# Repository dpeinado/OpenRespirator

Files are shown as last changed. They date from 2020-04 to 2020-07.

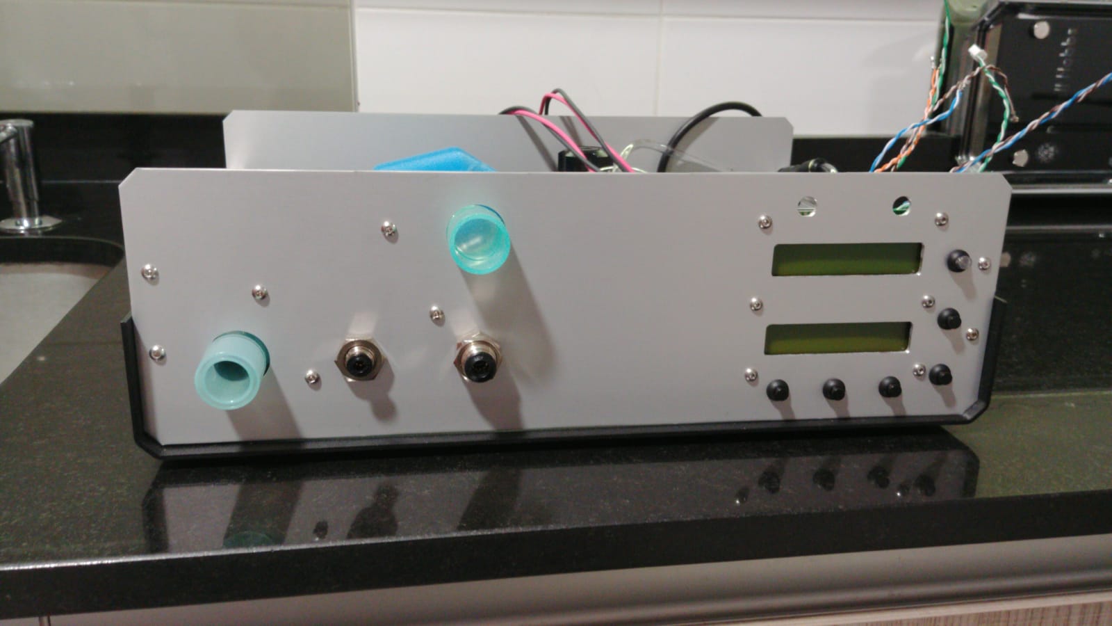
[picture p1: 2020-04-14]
Doc/Images/First assembly_4.jpeg

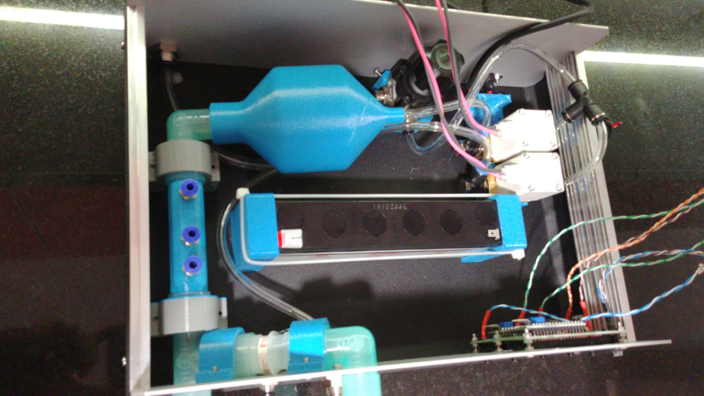
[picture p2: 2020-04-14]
Doc/Images/First assembly_5.jpeg

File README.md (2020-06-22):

# OpenRespirator
Software & Hardware for Open Respirator Project <br>

HW and system dodumentation are in the Doc directory <br>

## Contributors
- The system design is done by: Frede Jensen <br>
- Project coordination: Enrique Ramirez and Ramon Ruiz (Ennomotive) <br>
- Hardware & Software: David Ortiz, Rubén Perez de Aranda and Carlos Pardo <br>
- Collaborators: 
- - Intersurgical: Sara Rodriguez, Bill Barners, Mike Hinton <br>
- - Vithas Sanidad : Ignacio Narvaez <br>
- - McFly: Enrique, Marino y Daniel
  
## Sponsors: <br>

## ToDo list
### System

### Assembly

### Production
- Prepare production documentation
- - Define part alternatives
- Define production test & calibration
### Electronics
- Documentation
- - Electronics production test
### Firmware
- Monitor:
- Controller:
### Test & Validation
- Clinic test:
### Certification
- Documentation
- Presented to gobernment

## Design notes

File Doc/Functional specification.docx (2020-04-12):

# Emergency Ventilator

# Functional specification

Issue/change record

Issue | Date | Author | Reason of issue/summary
0.A | 10/04/2020 | | DRAFT, released for ongoing development

# Introduction

This document contains the full concept hardware and software design. The design is intended for the 75% of intensive care beds that are yet to be established in makeshift facilities.

# 1 Pressure Controlled SIMV

For purpose of simplicity, the ventilator operates in conventional Pressure Controlled SIMV (Synchronised Intermittent Mandatory Ventilation) mode of ventilation only. The ventilator will secure a set number of breaths per minute, by firstly attempting to synchronize the mechanical delivery of breaths with patient’s spontaneous efforts. If the patient fails to spontaneously take a needed breath, then the ventilator delivers it mandatorily.

To prevent a ‘fight’ between the patient and the ventilator, the ventilator reschedules the mandatory breath that follows a successfully synchronized spontaneous breath by 1 second.

SIMV behaves as PSV (Pressure Support Ventilation) when the patient makes full efforts, and it behaves as CMV (Continuous Mandatory Ventilation) if the patient does not make any efforts. When used with a mask on a conscious, spontaneously breathing patient, the SIMV behaves as nPSV or Synchronised BiPAP (by setting IP low). Switching the IP cycle off (or setting it equal to PEEP) makes SIMV behaves as CPAP (whether the patient is intubated or has a mask interface).

# 2 Functional specification

This section describes how the required performance characteristics (see General Description) are met.

### 2.1.1 User interface

The user interface is very simplified (and somewhat industrial looking). The top half of the facia is the monitoring interface. The bottom half is the controlling interface.

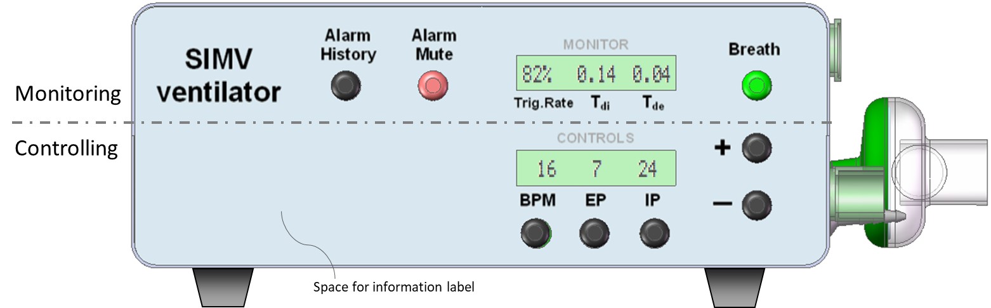
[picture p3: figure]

The process for adjusting a control paraments:

1. Press parameter control button.
2. Observe that the parameters value starts flashing (will time out after 5 sec inactivity).
3. Adjust the flashing parameter value using the +/- buttons.
4. Press parameter control button again to confirm the new setting.

The ‘Breath’ button has an integral green light. This flashes for 0.5s every time a spontaneous breath is detected. This provides an at a glance status of the patient, which can be seen at a distance across a room.

Pressing the green ‘Breath’ button delivers a manual breath. This is used to re-recruit the lung following a procedure that temporarily disconnected the patient from the ventilator, such as during suctioning or while changing the FiO2 level.

The ‘Alarm Mute’ button has an integral red light, which flashes under an alarm condition. Pressing the button will cancel the alarm event and suspend further alarms for 120 seconds.

The ‘Alarm History’ cycles through the last 10 alarm messages.

Alarm messages appear in the monitor (top) LCD display, where they overwrite the monitored parameters from 2.5 seconds every 3 seconds – i.e. the monitored values flash up for 0.5 seconds every 3 seconds while an alarm message is displayed.

The alarm message ‘Monitor Fail’ is detected by the controller and is displayed in the lower LCD.

Hospital staff commonly write information or place labels on their medical equipment, such as giving the device an identifiable name or number, or placing a reminder label. The facia is given a space for this. Below is an example reminder label that may be useful for certain personnel – without crowding the facia and detract from its simplicity.

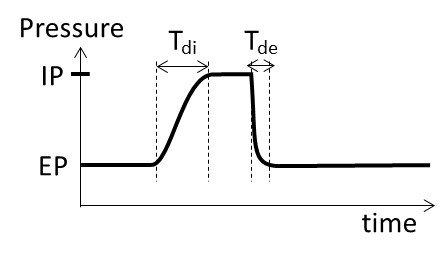
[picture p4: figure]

To power up the ventilator, press the ‘ON/OFF’ switch on the rear. Observe the power-up self-test correctly displays LEDs and the display digits.

To power down the ventilator, press the ‘ON/OFF’ switch on the rear. The monitor will display a message for 5 seconds saying ‘Power OFF?’. During this short period, press and hold any of the facia buttons for 2 seconds. If the 5-second message is missed, then simply flick the ‘ON/OFF’ switch again, to restart the 5-second message.

If none of the buttons are held for 2 seconds, or just pressed momentarily, the message will disappear and the ventilator will continue to operate under battery power. This enables moving the patient or intra-hospital transport.

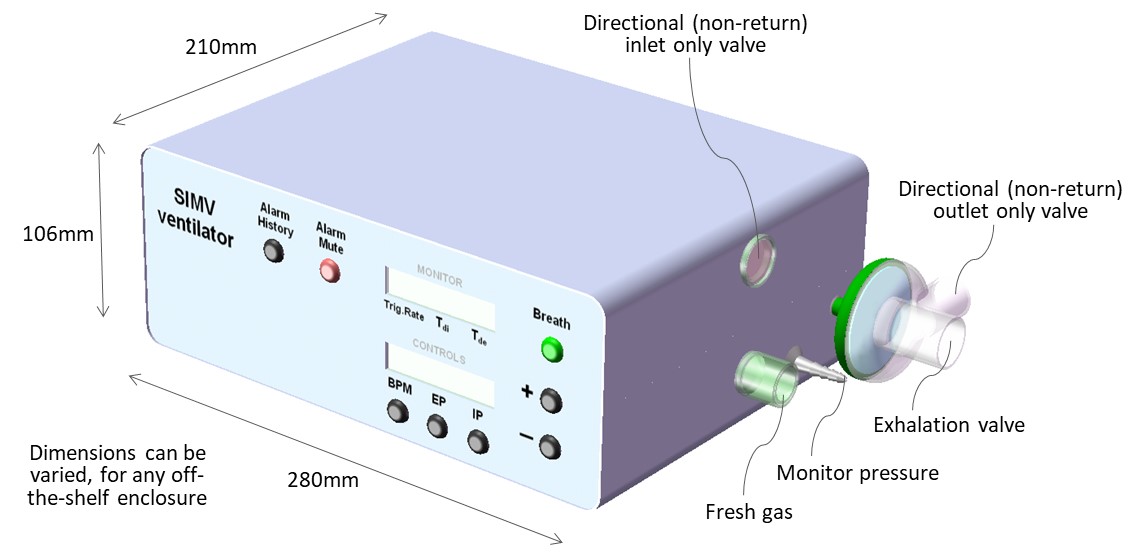
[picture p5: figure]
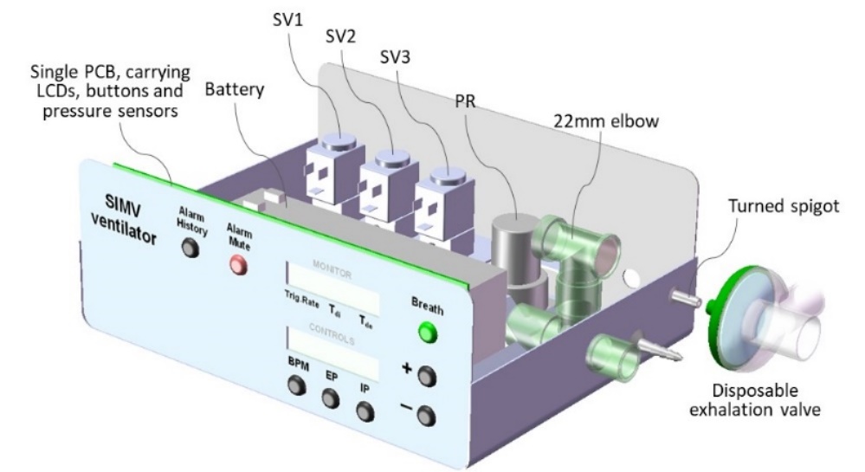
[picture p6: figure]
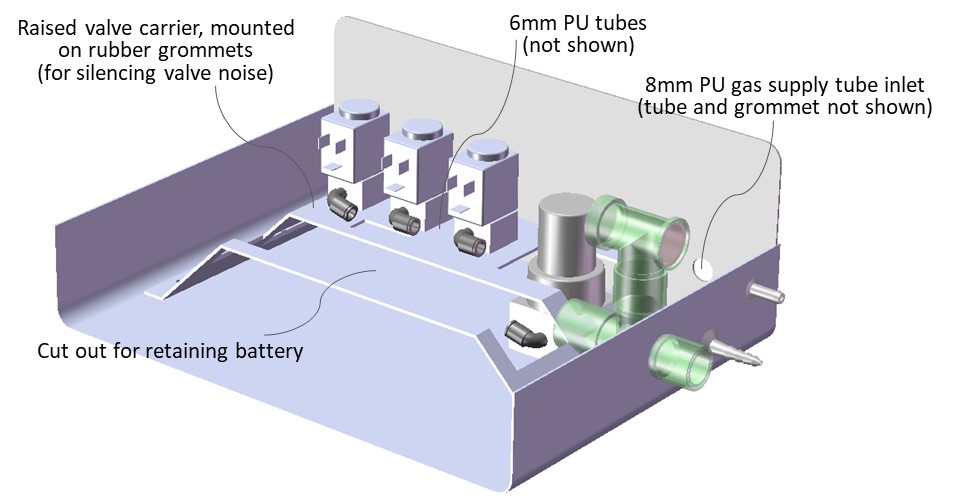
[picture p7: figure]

### 2.1.2 Schematic diagram

The Monitor and Controller operate independently, in parallel, observing each other (watchdogs). This assures the detection and alarming on any single failure mode. Both the controller and the monitor are capable of detecting an excess pressure (>40 mbar) and each can shut down the supply gas. This duality safeguards that compressed gas does not reach the patient circuit. All valves are NC (normally closed) types and will default to shutting off gas supply in case of total (battery) power failure.

The Controller operates its own user interface, for adjusting the parameters (BPM, EP and IP). The Controller reports its 3 parameters values every 50mS across an I2C serial interface with the Monitor. The Controller also reports when a valid change is made via the user interface. If the Monitor does not acknowledge receipt, then the Controller will instigate an alarm.

If the Controller reported ventilator paraments changes, without a prior valid user change, then it would indicate the Controller memory has corrupted. The Monitor will then alarm and can shut down gas supply if hazardous conditions occur.

The Monitor also calculates the triggered breath rate (patient effort) and the wave rise/decay times (Tdi and Tde, which indicates lung/system status). It will alarm if these deviate from tolerances.

On shut-down, the patient can breathe ambient air through the 2 directional NR valves.

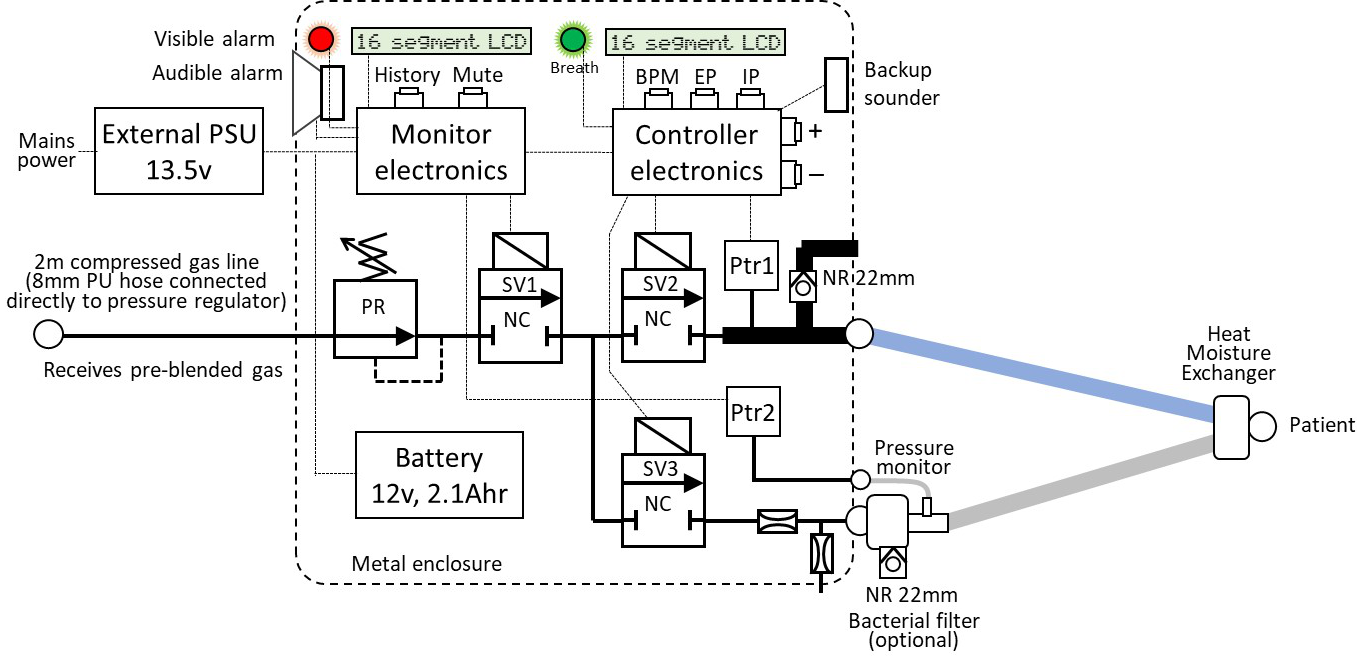
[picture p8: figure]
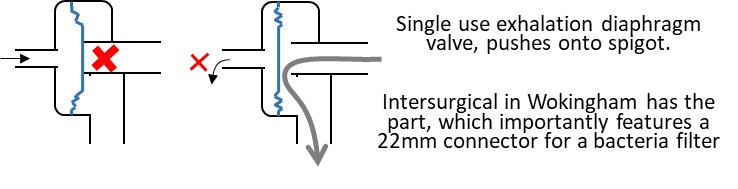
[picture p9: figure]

### 2.1.3 Ventilator operation flow chart

The Controller cycles the pressure wave in accordance with the set parameters (BPM, EP and IP). The inspiration cycle is instigated on breath detection, or if the mandatory cycle time is reached.

‘Open SV3’ has the effect of closing the exhalation valve – i.e. it should be read as ‘close exhalation valve’.

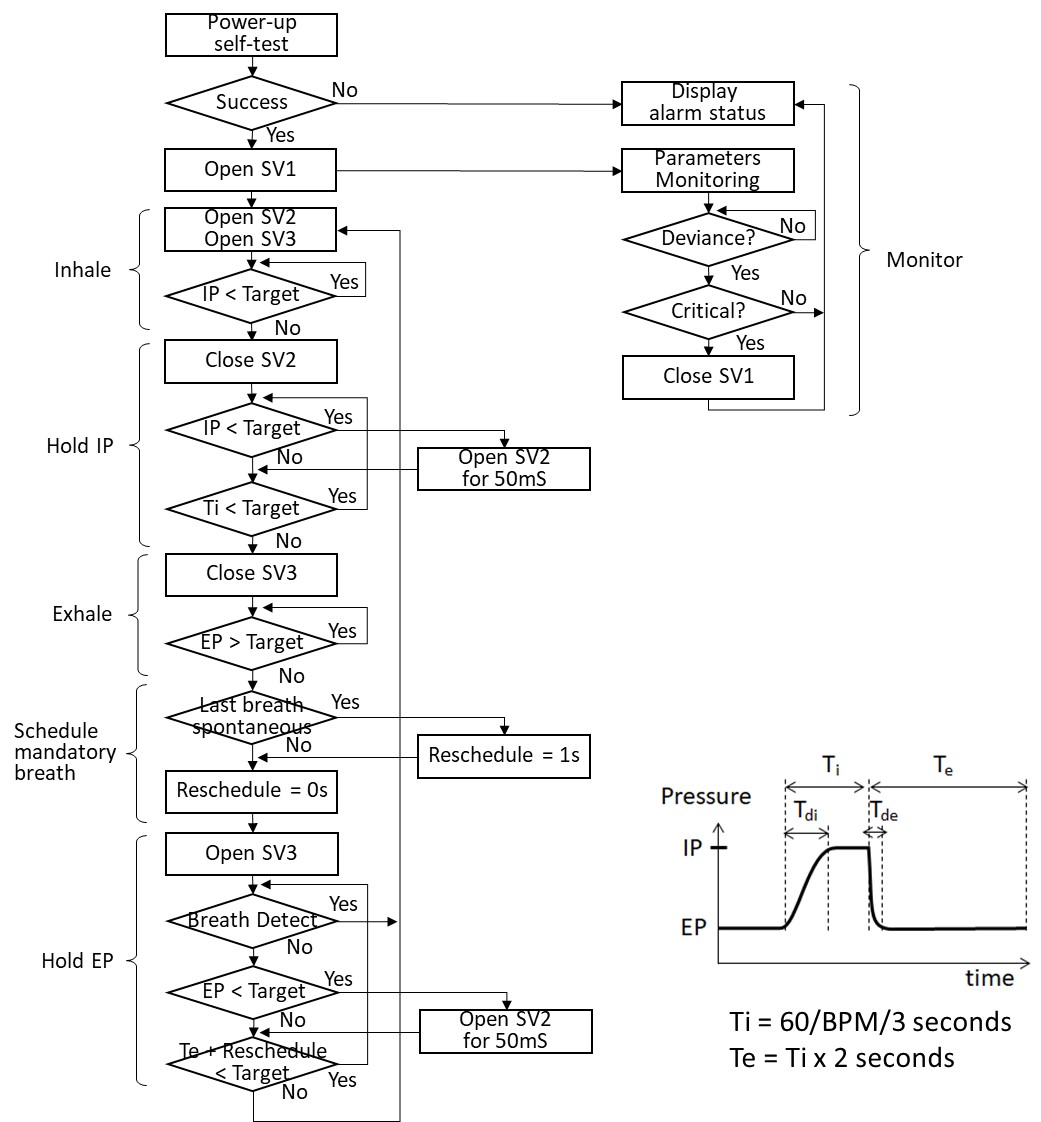
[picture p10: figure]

The steps ‘IP < Target’ and ‘EP > Target’ are likely to result is a small overshoot if implemented in their simplest form, due to the solenoid valve inertia/response time. The step will likely have some sub-steps to compensate for this, for example:

a) One approach: Once the ventilator user sets a new Target the initial breath cycle will use ‘IP < Target x 95%’. If this first breath undershoots, then the next cycle can be increased to ‘IP < Target x 96%). Keep incrementing until the intended IP is met and then freeze this setting. Do the same in reverse for reaching EP. The first cycle might use ‘EP > Target x 105%’ and then decrement this correction factor. Freeze the correction factor once the intended EP is reached. It could take 2 or 3 breaths for the ventilator to settle the IP and EP after a setting is changed.
b) Another approach, is to use testing and understanding of the overshoot and then build a fixed correction value into the software – i.e. the final compensation is applied to the very first breath cycle. A small variance can creep in if the IP rise time (Tdi) or EP decay time (Tde) changes/drifts, or if different solenoid orifice sizes are introduced. Such a small variance might be within tolerance and considered accurate enough. If not, the solution a) above is better at responding to the dynamics in the patient and circuit conditions.

The steps ‘Open SV2 for 50mS’ tops-up the patient circuit pressure, to compensate for leak in nSIMV/SyncBiPAP/CPAP with mask. In mask mode, this is will create a harmless ripple on the pressure plateaus. In fact, in HFOV and Bubble CPAP ventilation in infants, such type of pressure ‘vibration’ is reported to improve alveolar gas diffusion (makes ventilation more efficient).

The top-ups will not normally happen with an intubated patient, unless the circuit is incorrectly connected/faulty. The ventilator would indicate that top-ups are happening – hence, indicating a potential patient circuit problem.

In mask ventilation, the breath detection algorithm needs to discriminate between the patient breath effort and a top-up ‘ripple’. The former manifests as a small pressure drop, while the latter manifests as a small pressure rise – i.e. they are different and detectable, until they occasionally collide. Possibly, under large leak conditions, the breath detection sensitivity will have to be lowered, to prevent false triggers. Fortunately, mask ventilation is used primarily with strong breathing patients.

When making EP and IP the same value (showing IP as ‘OFF’), the ventilator is effectively in CPAP more and the IP steps can be by-passed. When the then patient breathes in, the pressure in the circuit reduces and SV2 will compensate by pulsing in fresh gas. When the patient subsequently exhales, the pressure in the circuit increases and valve SV3 will deactivate to exhaust the exhaled gas. This routine secures minimal gas/oxygen consumption in CPAP and BiPAP modes (contrary to conventional devices, which maintain about 15L/min continuous flow).

### 2.1.4 Pressure waveform specification

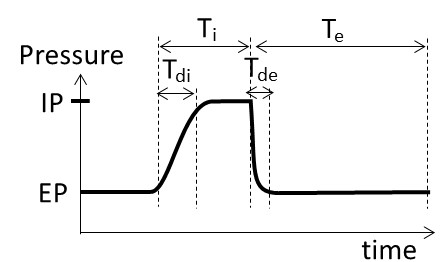
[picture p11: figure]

Ti (inspiratory time) varies between 0.7s (at 30 BPM) and 2s (at 10 BPM). Te (expiratory time) is 2 times Ti, according to the fixed 1:2 I:E ratio.

The ideal Tdi (inpspiratory pressure rise time) is about 0.3s, or 1/3 of the Ti, when ventilating a patient lung. Extending it to 0.45s would be tolerated and might make valve timing control easier. This equates to 60L/min inspiration flow rate. Beware if using a test lung with different compliance (e.g. a 5L plastic bottle) the Tdi will differ.

Tde should be as short as practically possible. The actual Tde depends on the lungs natural elasticity and resistance in the breathing circuit. As long as it looks reasonable sharp then the CO2 washout will happen.

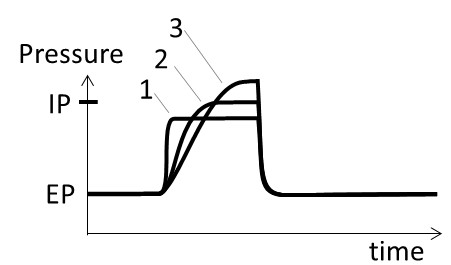
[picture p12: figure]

The rationale for Tdi is illustrated by the 3 waveform examples above. Each the 3 waves deliver about the same amount of ‘work’ and fill the lung with an equivalent volume of gas.

#1 uses the least pressure (which is good), but the abrupt rise is faster than the lung can comply. This risks putting shear stress on the lung tissue.

#3 produces a gentler rise (which is good), but it requires a higher plateau (which is bad) because the lung tissue is sensitive to pressure (barotrauma).

#2 is the best compromise. The plateau should ideally be about 2/3 of the Ti time, but should be compromised to 60L/min flow rate. With the fastest Ti being 0.67s, the best fixed Tdi = 0.45s.

A 5L plastic bottle test lung tends to be less compliant and fills more straightforwardly (compared to the intricate lung). Development testing should probably focus on Tdi = 0.2s. Tdi is adjusted by regulator PR, or by changing the orifice size in SV1 and/or SV2 (preferably they are kept the same).

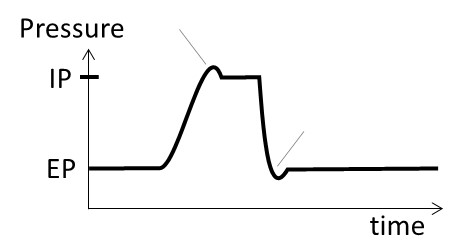
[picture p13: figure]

Small over-/under-shoot spikes are tolerated, but undesirable. An IP overshoot larger than 3 mbar is not tolerated. There are actually special modes of ventilation that has a lower IP plateau combined with a larger overshoot, and there are modes that deliberately undershoot the initial EP plateau (to help CO2 washout). However, these are specialist modes and not should be default in an emergency ventilator.

Lastly, it is one thing to re-produce the pressure waveform. It must be simultaneously assured that inhaled gas comes from the fresh supply side and that exhaled gas is entirely directed into the exhaust path. The patient must not rebreathe the same gas, which would become increasingly oxygen depleted and CO2 enriched (results in suffocation). Many ventilators have a continuous flush flow through the circuit; but this is omitted in this design, to preserve oxygen (in short supply).

### 2.1.5 Alarm signals

The signals are specified by international standard IEC 60601-1-8. The priority level is assigned according to the following table from the standard:

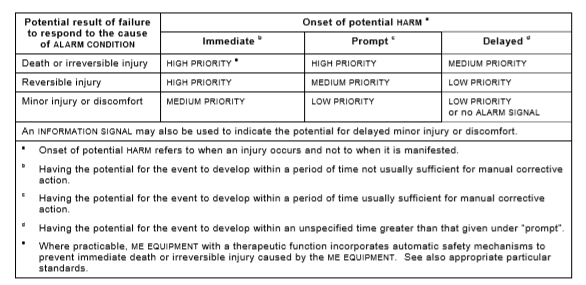
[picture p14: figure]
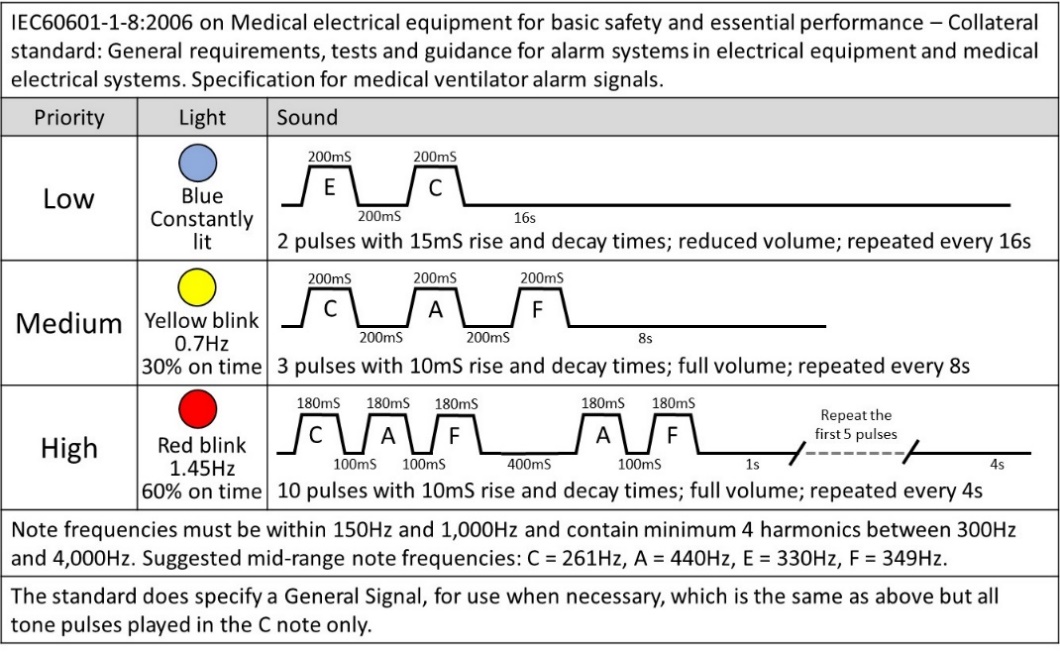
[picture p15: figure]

It is acceptable for an emergency ventilator to deviate from the standard. The alarm sounder in this design conforms to the standard pulse lengths, but it will be played in a single tone – aligning to the ‘general’ tone specified in the standard (although not the tone rise/decay) – i.e. it plays the correct melody, but in just one note. This simplifies construction and the development time.

It is proposed to use a single colour alarm light, but to pulse it in compliance with the standard.

### 2.1.6 Components

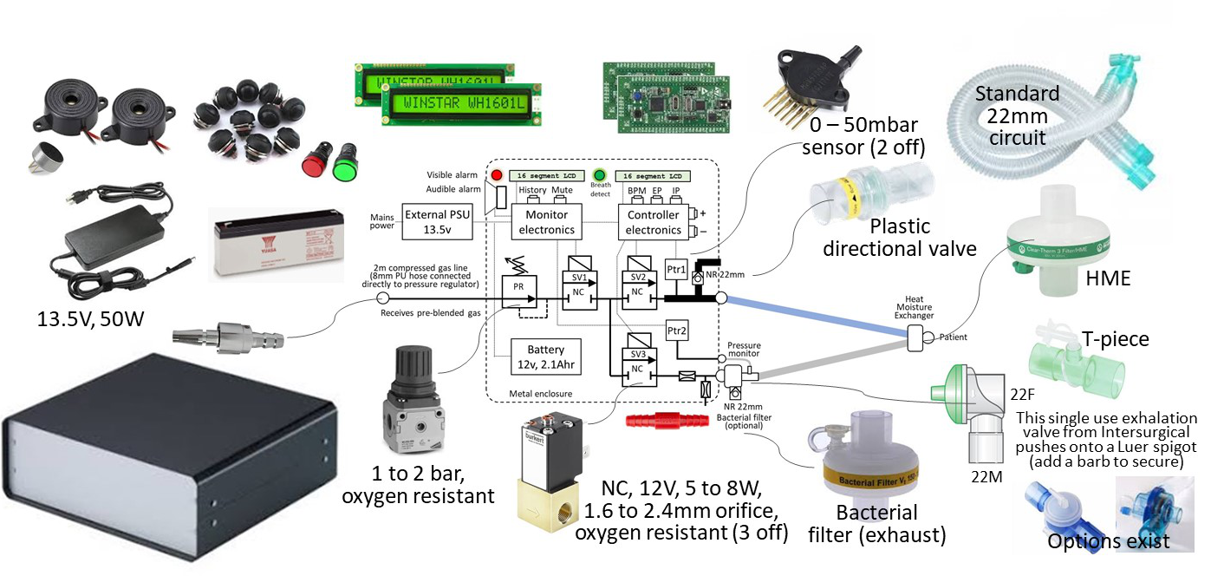
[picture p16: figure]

All components are available off-the-shelf at most national levels. Total components cost for the ventilator are approximately £400 (GBP), or Eu460 or US$500. Each patient circuit has a component cost of £12 (GBP), at trade prices. The Bill of Materials is included in Appendix 1.

Components are selected for having known acceptable electro-magnetic characteristics in other applications (to enable omission of time-consuming EMC qualifications).

The design is highly tolerant to alternative brands and specification variances. For example:

- The pressure regulator can be any brand that is oxygen resistant and is adjustable between 1 and 2 bar (15 and 30psi), while being stable. Possibly a relieving type is most stable, but a non-relieving can be acceptable. The low cost (£14) type shown above is fine. Small and cheap (£8) regulators (the type measuring less than 15mm across) tend to be less stable and are likely unsuitable.
- The solenoid valves simply need to reliably open and close in 20mS or less. There is no need for a fast 3mS response. The valves must of course have oxygen resistant seals. The orifice size can be between 3mm and 4mm (needs validating), but should preferably be the same across all 3 valves, for sourcing and production simplicity. If the sizes must vary, then ensure that SV1 has the largest orifice and SV3 has the smallest orifice. SV2 can then be anything in between. Set up by ventilating into 5L plastic bottle (representing a test lung). Adjust the pressure regulator until the PIP rise time (Tdi) is 0.12 second (this will become slightly longer into a real lung, which is more compliant than a plastic bottle). This adjustment of the pressure in effect compensates for the orifice sizes. Note, that target for inspiration flow rate is 60L/min, which produces a Tdi = 0.45 into a 600ml lung. Simply adjust the pressure regulator to the desired level. Mount the valves on noise reducing rubber grommets.
- The power supply and battery must be 13.5v and 12v respectively, but any brand and shape are accepted. The specified 2.1Ahr battery can be changed to a different size, but beware that the 45 min battery backup time will be affected.

All patient circuit parts are readily available from a number of medical plastics suppliers across the world. In the UK and Norther Ireland, these would include Intersurgical, Flexicare, Armstrong and/or Europlaz. There are many others around the world.

The 22mm patient connector ports must conform to the international standard (summarised here).

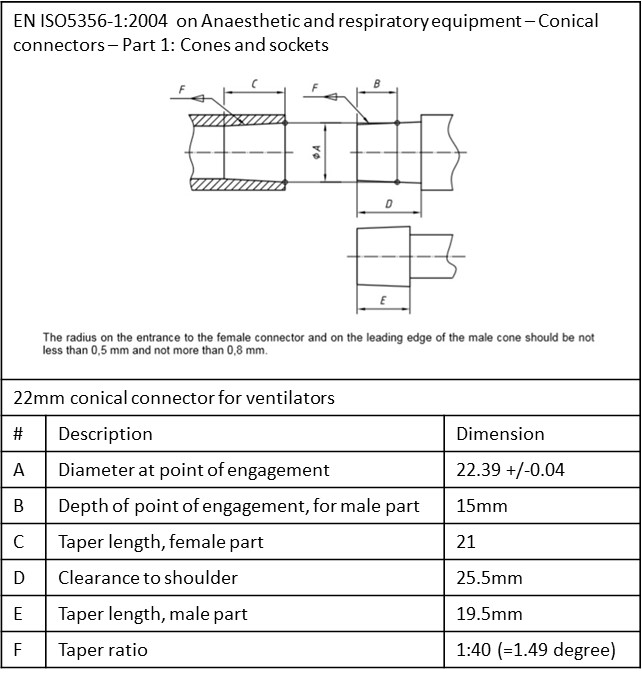
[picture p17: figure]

### 2.1.7 Critical parts

The following identified the critical parts, in accordance with IEC 60601-1 and IEC 60601-2-12.

Any substitutions must meet the same rating, or better, and related standards.

# | Component | Function | Manufacturer and model | Technical Rating | Standards

1 | Pressure regulator | todo | | Clean, oxygen resistant,
2 | Solenoid valve
3 | Flow restricting orifice
4 | Pneumatic tubing | | | Oxygen resistant. Rated >10bar.
5 | Directional valve
6 | Fresh gas port | | | 22mm Male conical connector | IEC 5356-1
7 | Power supply unit
8 | Battery
9 | Pressure transducer
10 | Micro-processor
11 | FET transistor | | | Transient diode
12 | Resistors (general) | | | Rated min 125mW
13 | Capacitors (general) | | | Rated min 50v
14 | Alarm sounder
15 | Microphone
16 | Push buttons | | | Rates > 10,000 cycles
17 | LCD
18 | Indicator lights (alarm, breath)
19 | Case | | | No water ingress | IEC 60601-???

### 2.1.8 Electronic design

The following diagrams (next page) suggests using a Microchip PIC controller. Any alternative microcontrollers with the appropriate number of General Purpose in/out ports and an ADC port can be used.

The Monitor instigates a serial I2C data exchange with the Controller every 50mS. It receives the set Control parameters in return. The Monitor and Controller electronics are electrically separated by at least a 4mm gap. A failure in one unit will not electrically influence the other over the I2C data lines.

Both the Monitor and the Controller (ADC) measure the pressure sensors analogue signal every 2mS.

When the monitor alarms it listens (microphone) for the speaker sound to appear. In case of a no-sound failure, the Monitor requests the Controller to sound the backup sounder.

The Controller will sound the backup sounder and display ‘Monitor Error’ if the Monitor does not poll it for 100mS.

The SLA (sealed lead acid) battery is continually float charging at 13.5V. This avoids a battery management circuitry and simplifies the design.

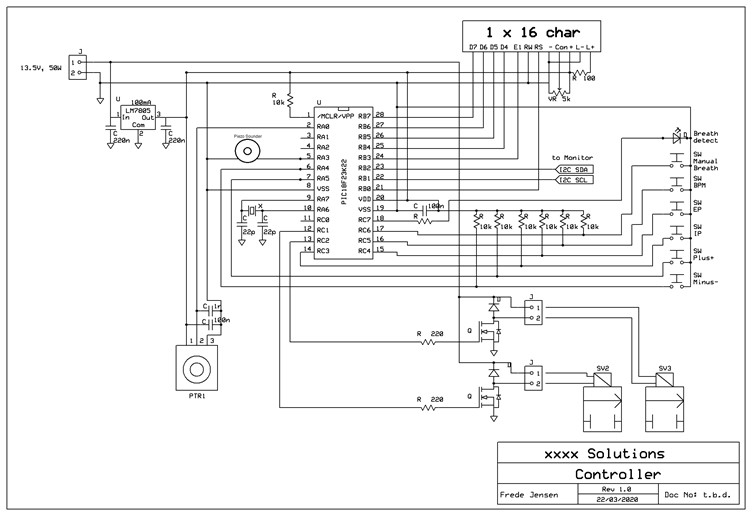
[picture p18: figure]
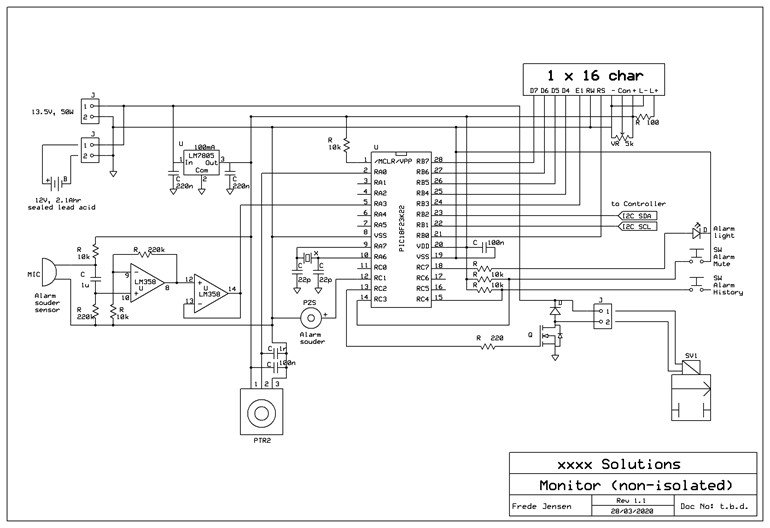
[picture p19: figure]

### 2.1.9 Firmware flow – Level 1 – flow chart

The operational flow chart shown in section 1.4.3 is not complex to implement, for a skilled software/firmware developer. Although the development is an emergency, the fundamental principles of international standard IEC 62304 on medical device software life-cycle processes should be observed.

### 2.1.10 Firmware flow – Level 2 – psudo code

To be developed. It is assumed that all standard medical software precautionary routines are used, such as 3 best of 5 tests for values stored in EEPROM cells (i.e. 1 value is stored 5 times, of which a test verifies that at least 3 are the same, before being applied).

#### 2.1.10.1 Breath detection algorithm

Pressure wave breath detection uses a commonly known algorithm, which is well tested in existing marketed medical ventilators. It involves filtering/integrating the real-time patient circuit pressure into two mean values in the Controller: one is fast with a 50mS time-constant and the other is slow with a 2000mS time-constant. When the patient breathes in the circuit pressure will momentarily drop. The fast filter/integrator output will drop faster, and ‘cross’ below the slow filter output. An offset is added to the fast filter value. This offset determines the breath detection sensitivity. If the offset is too small then the algorithm risks creating false triggers (from underlying sensor/measurement noises). If the offset is too large then the algorithm risks missing a weak patient effort and the detection is delayed (less synchronized and supportive to the patient). The Controller should report the detection rate to the Monitor, for comparison and display (and alarm if they mismatch).

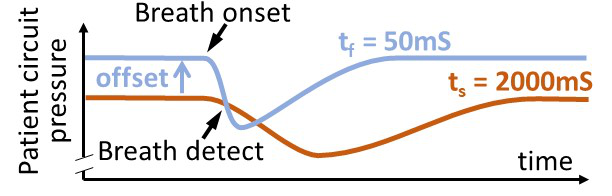
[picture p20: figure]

Its pseudo-code is included here for information:

BEGIN {ISR}

Save context: working, status, and program counter registers

IF interrupt = I2C buffer full

Call I2C_HANDLE

ENDIF

Pressure = ADC port value

IF pressure > 40 mbar

Call SHUTDOWN

ENDIF

Pressure_fast = Mean for last 25 Pressure values

Pressure_slow = Mean for last 1000 Pressure values

Offset = 3 mbar // Declare as a constant. Test for best result

IF (Pressure_fast + Offset) < Pressure_slow

Breath_detect = TRUE

ENDIF

[…] // Add other routines here

Restore context: working, status, and program counter registers

Clear interrupt flag

RETURN from interrupt

END {ISR}

BEGIN {MAIN}

Call CONFIG_MPU_REG

Call INITIALIZE_VARIABLES

Call INITIALISE_ISR // Set to ISR call to every 2mS

WHILE 0

Call USER_INTERFACE

[…] // Add other routines here

ENDWHILE

END {MAIN}

Routines for calculating the P_short and P_long mean values:

If using floating points math (called every 2mS):

[…]

Pressure = ADC port value

temp = P_fast/25

P_fast = P_fast – temp + (Pressure/25)

temp = P_slow/1000

P_slow = P_slow – temp + (Pressure/1000)

[…]

If using fixed points math (called every 2mS):

[…]

Pressure = ADC port value

Add Pressure to P_fast_buffer[25] // Overwrite the buffer tail, move tail pointer

P_fast = (Sum of P_fast_buffer[25]) / 25

Increment ISR_call_count

IF ISR_call_count = 40 // Only use 1 in 40 measured values

Add Pressure to P_slow_buffer[25] // Overwrite the buffer tail, move tail pointer

P_slow = (Sum of P_slow_buffer[25]) / 25

ISR_call_count = 0

ENDIF

[…]

#### 2.1.10.2 Tdi and Tde detection and measurement

Similar to breath detection, maintain 2 filters/integrator in the Monitor: one is fast with a 50mS time-constant and the other is slow with a 300mS time-constant. When P_fast = P_slow then we are at a pressure plateau level. When P_fast > P_slow then we are in a Tdi phase. When P_fast < P_slow then we are in a Tde phase. Start and stop time counters at each phase change. You would average the values over the last 10 seconds of operation. Disregard any rogue values (appears more the +/-10% of the average). This will still detect a natural, gradual drift.

### 2.1.11 Firmware flow – Level 3 – source code

The full source code is included in the Appendix 2 can be downloaded from here: www…..

### 2.1.12 Software bug register

### 2.1.13 Labelling

The back of the device must carry the information stipulated in regulatory requirements for ventilators. It is assumed that the regulatory qualification will be short-cut and that CE-marking might not be completed. Residual risks are described in the user manual and service manual.

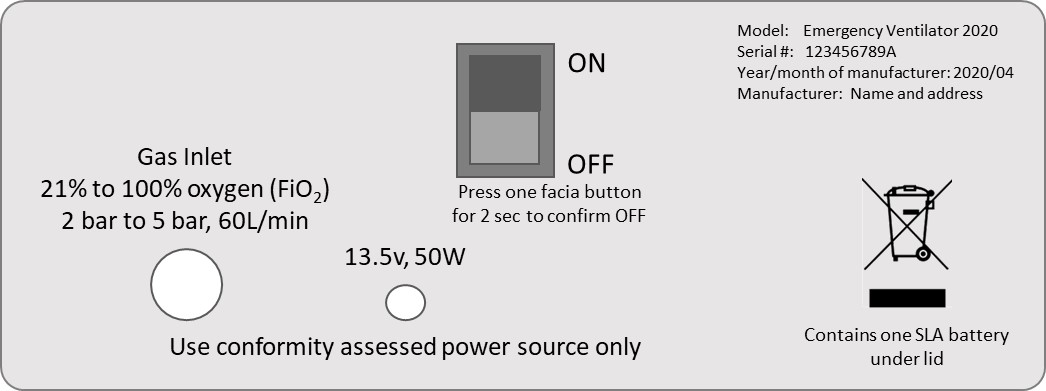
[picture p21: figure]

The fresh gas port is labelled ‘Gas Output’.

The exhalation control port is labelled ‘Gas Return’

The Monitor pressure port is labelled ‘Patient Pressure’.

### 2.1.14 Durability of markings

For testing purpose, markings are rubbed by hand, without undue pressure, first for 15 seconds with a cloth rag soaked with distilled water, then for 15 seconds with a cloth rag soaked with methylated spirit and then for 15 seconds with a cloth rag soaked with isopropyl alcohol. The markings must not deteriorate.

### 2.1.15 Packaging

Protect contain maintain contamination status. Todo

### 2.1.16 Clinical procedure

The ventilator is designed for simplified mass-ventilation, with an operating principle that supports a deskilled (skill-divided) clinical process. This process frees-up the most skilled clinicians from hands on activities, in part to enable them focusing on a maximum number of patients, and in part to reduce their exposure to patient contaminants. In crude terms, it is easier to replace a lower skilled assistant than it is to replace a doctor.

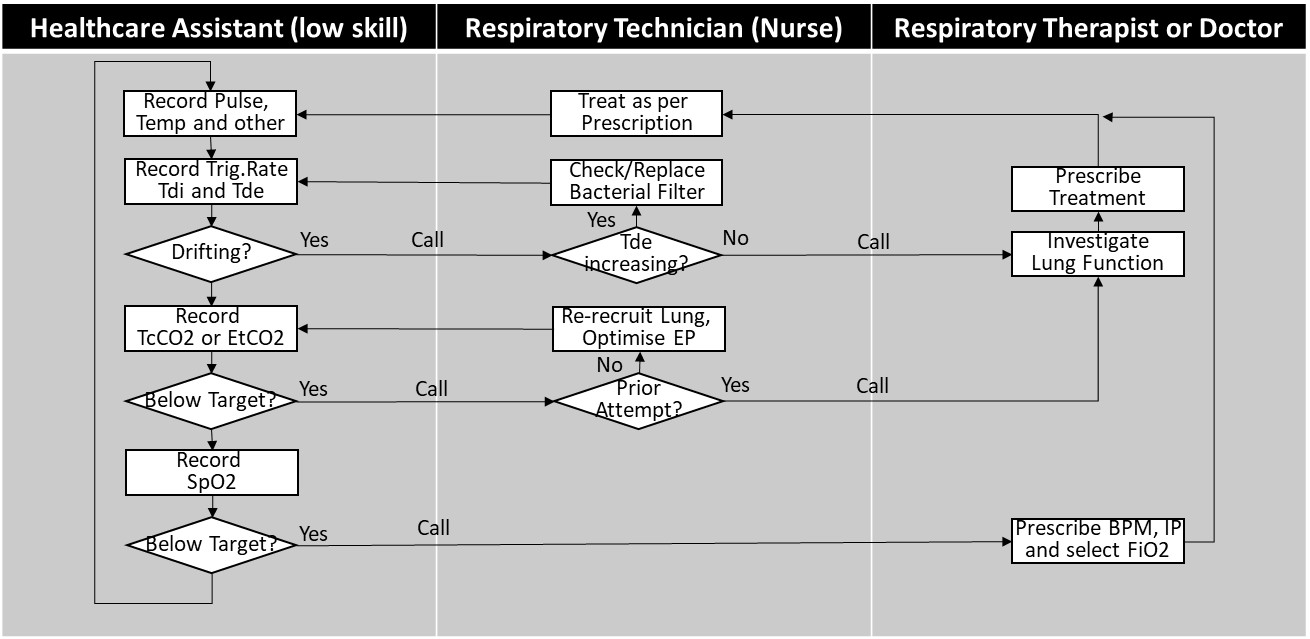
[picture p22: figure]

A drift in the Trigger Rate would indicate a change in the patient’s overall condition. It can be seen as a measure of stabilisation and recovery – or an indication that a rescue therapy is required.

A drift in the Tdi (IP rise time) and/or Tde (expiration wave decay time) indicates that the lung condition is changing. A shortening in Tdi would indicate a worsening of the lung condition, such as respiratory distress or a build-up of fluid or puss (which would need clearing out by a suctioning procedure). They could also indicate a problem in the patient circuit or the exhaust bacterial filter.

Selecting a different FiO2 level requires that the ventilator is temporarily disconnected from one supply and connected to another (in a matter of seconds). The Respiratory Technician should subsequently press and hold the ‘Manual Breath’ button once for 2 seconds, to re-recruit the lung.

‘Optimise EP’ is done by increasing the EP by 4 or 5 mbar. Then reduce EP by 1 mbar and observe the resulting TcCO2 or EtCO2 value for 15 – 20 seconds (until settled). Repeat and observe how the CO2 elimination improves with each step, until it suddenly worsens. Return EP to the vale that produced the best CO2 elimination. Then press and hold the ‘Manual Breath’ button once for 2 seconds, to ensure that the lung is fully recruited. A simple procedural manoeuvre.

# Appendix 1 – Bill of Materials

# | Schematic | Description | Manufacturer | Manufacturer code | Source | Link | Catalogue number

1 | PR | Pressure regulator, G1/4 | SMC | ARX2-0-F02 | RS components | https://uk.rs-online.com/web/p/pneumatic-regulators/0209187/ | RS 209-187
2 | SV1 | Solenoid valve, 2/2 NC, 2.4mm, 5W | SMC | VX212AZ1D (4mm orifice) | RS components | https://uk.rs-online.com/web/p/solenoid-valves/8407020/ | RS 840-7020
3 | SV2 | Solenoid valve, 2/2 NC, 2.4mm, 5W | SMC | VX212AZ1D (4mm orifice) DRAFT – not definitive | RS components | https://uk.rs-online.com/web/p/solenoid-valves/8407020/ | RS 840-7020
4 | SV3 | Solenoid valve, 2/2 NC, 2.4mm, 5W | SMC | VX212AZ1D (4mm orifice) | RS components | https://uk.rs-online.com/web/p/solenoid-valves/8407020/ | RS 840-7020
5 | FR1 | Filtered orifice restrictor, 0.025" | Air logic | F-950-73-251-B80 | Make equivalent
6 | FR2 | Filtered orifice restrictor, 0.016" | Air logic | F-950-73-161-B80 | Make equivalent
7 | EV1 | Exhalation control valve | Intersurgical | 1922501 | Intersurgical
8 | NR1 | Directional non-return valve 22M,22M | Intersurgical | 1950 | Intersurgical
9 | NR2 | Directional non-return valve 22M,22M | Intersurgical | 1950 | Intersurgical
13 | PTR1 | Pressure tranducer, 40mbar, amplified | Freescale Semiconductor | MPXV5004GP | RS components | https://uk.rs-online.com/web/p/differential-pressure-sensor-ics/7191166/ | RS 719-1166
14 | PTR2 | Pressure tranducer, 40mbar, amplified | Freescale Semiconductor | MPXV5004GP | RS components | https://uk.rs-online.com/web/p/differential-pressure-sensor-ics/7191166/ | RS 719-1166
15 | U1 | t.b.d. | t.b.d. | t.b.d. | t.b.d.
16 | U2 | t.b.d. | t.b.d. | t.b.d. | t.b.d.
17 | PSU | External power supply, 13.5v, 4A (50W) | t.b.d. | t.b.d. | RS components | https://uk.rs-online.com/web/p/desktop-power-supplies/7649113/ | RS 764-9113
18 | BATT | Sealed Lead Acid, 12v, 2.1Ahr | Yuasa | NP2.1-12 | RS components | https://uk.rs-online.com/web/p/lead-acid-batteries/0597813 | RS 597-813
19 | SPK | Mylar speaker, 1W, 8 ohm | t.b.d. | t.b.d. | RS components | https://uk.rs-online.com/web/p/speaker-drivers/6284529/ | RS 628-4529
20 | PZS | Continuous Piezo Buzzer | t.b.d. | t.b.d. | RS components | https://uk.rs-online.com/web/p/piezo-buzzer-components/6173097/ | RS 617-3097
21 | MIC | Electret microphone, pcb mount | t.b.d. | t.b.d. | RS components | https://uk.rs-online.com/web/p/condenser-microphone-components/7243125/ | RS 724-3125
22 | LCD1 | Alphanumeric LCD, 1 Row by 16, green | Fordata | FC1601E01-FHYYBW-51LE FC | RS components | https://uk.rs-online.com/web/p/lcd-monochrome-displays/1253297/ | RS 125-3297
23 | LCD2 | Alphanumeric LCD, 1 Row by 16, green | Fordata | FC1601E01-FHYYBW-51LE FC | RS components | https://uk.rs-online.com/web/p/lcd-monochrome-displays/1253297/ | RS 125-3297
24 | TB1 | Air Hose Clear Polyurethane 8mm OD, 2m length | RS components | RS 917-2404 | RS components | https://uk.rs-online.com/web/p/air-hose/9172400/ | RS 917-2404
25 | TB2 | Air Hose Clear Polyurethane 6mm OD, about 30cm length | RS components | RS 917-2400 | RS components | https://uk.rs-online.com/web/p/air-hose/9172400/ | RS 917-2400
26 | TB3 | Air Hose Clear Polyurethane 6mm OD, about 30cm length | RS components | RS 917-2407 | RS components | https://uk.rs-online.com/web/p/air-hose/9172407/ | RS 917-2407
27 | CN1 | Elbow 22F, 6mm, 22M | Intersurgical | 1893
28 | CN2 | Elbow 22M, 22F | Intersurgical | 1992
29 | CN3 | T-piece 22M, 6mm, 22F | Intersurgical | 1963
30 | CN4 | Straight connector, 8mm to 1/4 thread | RS components | RS 916-0729 | RS components | https://uk.rs-online.com/web/p/pneumatic-straight-fittings/9160729/ | RS 916-0729
31 | CN5 | Elbow connector, 6mm to 1/4 | RS components | RS 176-1404 | RS components | https://uk.rs-online.com/web/p/pneumatic-straight-fittings/1761404/ | RS 176-1404
32 | CN6 | Elbow connector, 6mm to 1/8 | RS components | RS 916-0858 | RS components | https://uk.rs-online.com/web/p/pneumatic-elbow-fittings/9160858/ | RS 916-0858
33 | CN7 | Elbow connector, 6mm to 1/8 | RS components | RS 916-0858 | RS components | https://uk.rs-online.com/web/p/pneumatic-elbow-fittings/9160858/ | RS 916-0858
34 | CN8 | T-connector, 6mm, 6mm, 1/8 | RS components | RS 916-0808 | RS components | https://uk.rs-online.com/web/p/pneumatic-t-fittings/9160808/ | RS 916-0808
35 | CN9 | Elbow connector, 6mm to 1/8 | RS components | RS 916-0858 | RS components | https://uk.rs-online.com/web/p/pneumatic-elbow-fittings/9160858/ | RS 916-0858
36 | CN10 | T-connector 6mm, 4mm, 6mm | RS components | RS 176-1376 | RS components | https://uk.rs-online.com/web/p/pneumatic-tee-tube-to-tube-adaptors/1761376/ | RS 176-1376
37 | CN11 | Elbow connector, 6mm to 1/8 | RS components | RS 916-0858 | RS components | https://uk.rs-online.com/web/p/pneumatic-elbow-fittings/9160858/ | RS 916-0858
38 | CN12 | Elbow connector, 6mm to 1/8 | RS components | RS 916-0858 | RS components | https://uk.rs-online.com/web/p/pneumatic-elbow-fittings/9160858/ | RS 916-0858
39 | CN13 | Elbow connector, 6mm to 1/8 | RS components | RS 916-0858 | RS components | https://uk.rs-online.com/web/p/pneumatic-elbow-fittings/9160858/ | RS 916-0858
40 | CN14 | Elbow connector, 6mm to 1/8 | RS components | RS 916-0858 | RS components | https://uk.rs-online.com/web/p/pneumatic-elbow-fittings/9160858/ | RS 916-0858
41 | CN15 | Pneumatic Quick Connect Coupling Brass 1/4 | RS components | RS 667-1730 | RS components | https://uk.rs-online.com/web/p/pneumatic-quick-connect-couplings/6671730/ | RS 667-1730
42 | ENC | Metal case 280 x 210 x 106 | t.b.d. | t.b.d. | RS components | https://uk.rs-online.com/web/p/instrument-cases/7694902/ | RS 769-4902

# Appendix 2 – Source code

Insert source code, the whole 20 – 30 pages of it

Title: Emergency Ventilator Date: 10 Apr 2020 Subject: Functional specification Issue: 0.A Doc No. [DRAFT] Page: 20 of 24

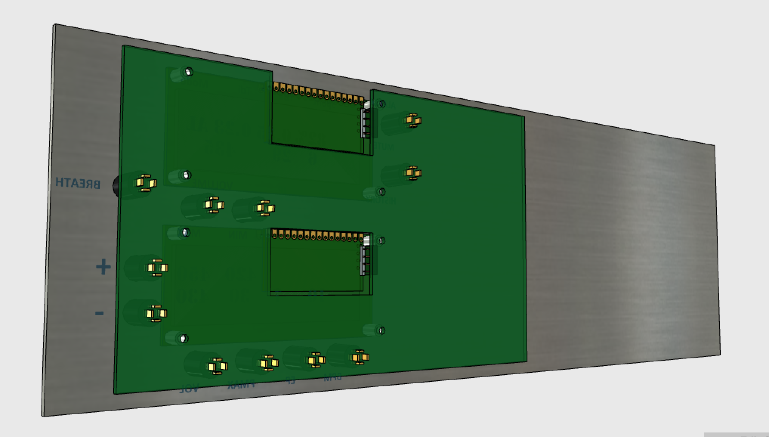
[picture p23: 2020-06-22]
Doc/Images/Captura de pantalla 2020-04-20 18.26.33.png

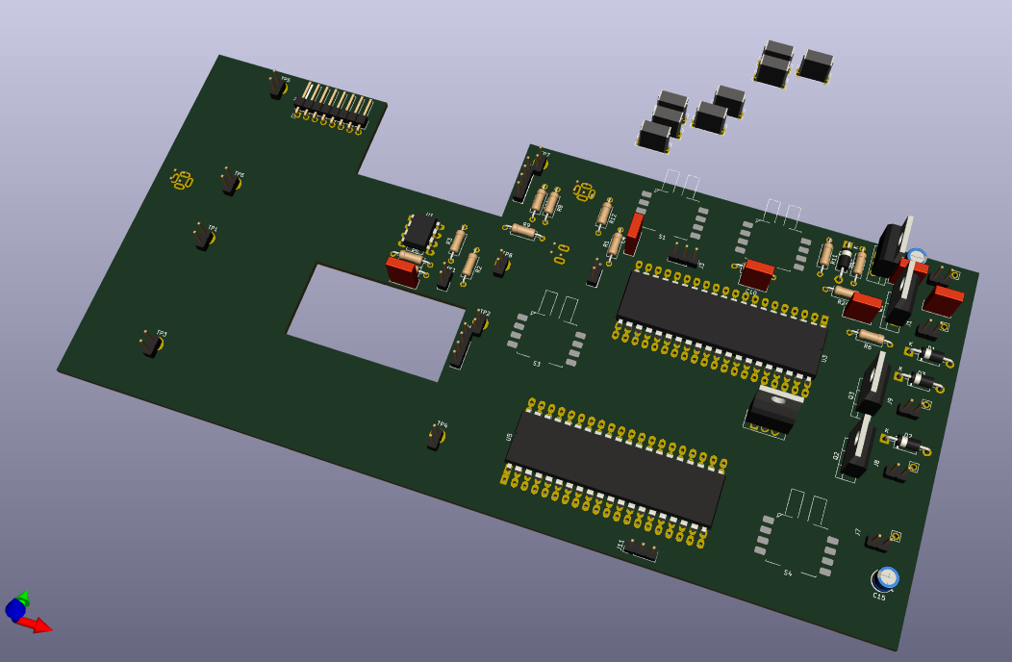
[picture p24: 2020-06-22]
Doc/Images/Captura de pantalla 2020-04-20 18.28.09.png

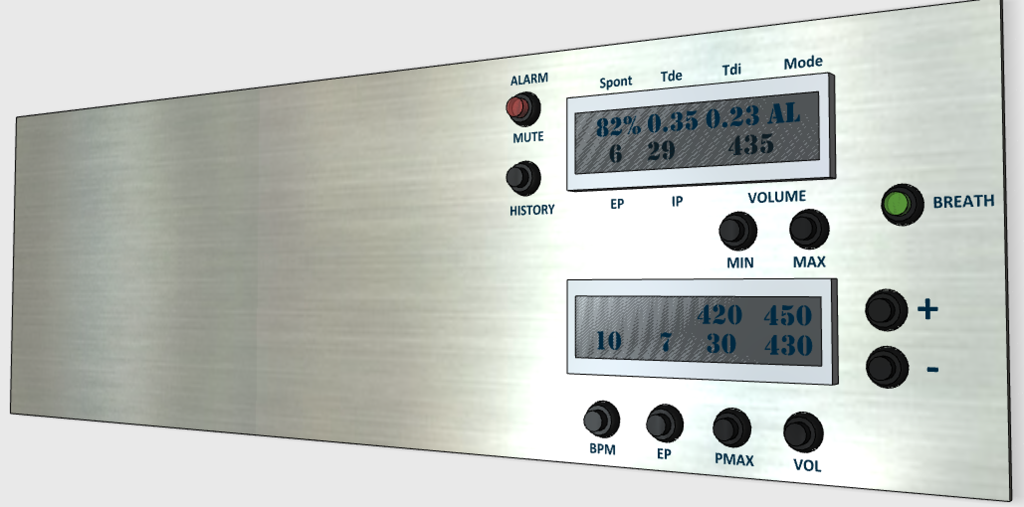
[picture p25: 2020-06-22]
Doc/Images/Captura de pantalla 2020-04-20 18.25.56.png

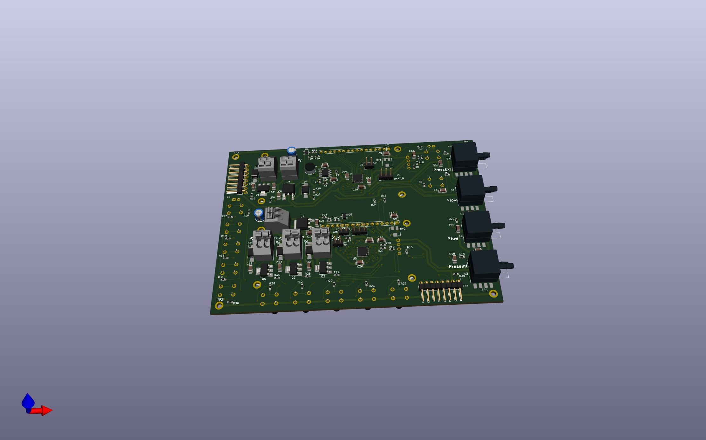
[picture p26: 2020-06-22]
Doc/PCB/Main_Board_v1_1_SMD/Main_Board_v1_1_smd.jpg

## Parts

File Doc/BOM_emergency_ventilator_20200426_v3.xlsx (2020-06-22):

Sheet: BOM
Bill of material |  |  |  |  |  |  |  |  | 1.10 | exchange rate
# | Schematic | Description | Manufacturer | Manufacturer code | Source | Link | Catalogue number | Unit price (GBP) | Unit price (Euro) | Comment
1 | PR | Pressure regulator, G1/4 | SMC | ARX2-0-F02 | RS components | https://uk.rs-online.com/web/p/pneumatic-regulators/0209187/ | RS 209-187 | 14.52 | 15.97 | Any equivalent, oxygen resistant and clean
2 | SV1 | Solenoid valve, 2/2 NC, 2.4mm, 5W | SMC | VX212AZ1D (4mm orifice) | RS components | https://uk.rs-online.com/web/p/solenoid-valves/8407020/ | RS 840-7020 | 24.67 | 27.14 | Any equivalent, oxygen resistant and clean. Make sure the spring /coil is rated to close at 30psi (2bar). Bigger orifice = stronger spring = more porwerful coil.
3 | SV2 | Solenoid valve, 2/2 NC, 2.4mm, 5W | SMC | VX212AZ1D (4mm orifice) | RS components | https://uk.rs-online.com/web/p/solenoid-valves/8407020/ | RS 840-7020 | 24.67 | 27.14 | Any equivalent, oxygen resistant and clean. Make sure the spring /coil is rated to close at 30psi (2bar).
4 | SV3 | Solenoid valve, 2/2 NC, 2.4mm, 5W | SMC | VX212AZ1D (4mm orifice) | RS components | https://uk.rs-online.com/web/p/solenoid-valves/8407020/ | RS 840-7020 | 24.67 | 27.14 | Any equivalent, oxygen resistant and clean. Make sure the spring /coil is rated to close at 30psi (2bar).
5 | FR1 | Filtered orifice restrictor, 0.025" | Air logic | F-950-73-251-B80 | Make equivalent |  |  | 3.00 | 3.30 | For prototyping, turn a plastic piece and drill a 0.6mm orifice, in 2mm thick wall
6 | FR2 | Filtered orifice restrictor, 0.016" | Air logic | F-950-73-161-B80 | Make equivalent |  |  | 3.00 | 3.30 | For prototyping, turn a plastic piece and drill a 0.4mm orifice, in 2mm thick wall
7 | EV1 | Exhalation control valve | Intersurgical | 1922501 | Intersurgical |  |  | 1.60 | 1.76 | Show in part 1414 in Intersurgical CC catalogue page 52. Might need alternative, 3D print
8 | NR1 | Directional non-return valve 22M,22M | Intersurgical | 1950 | Intersurgical |  |  | 0.90 | 0.99 | Page 55 in Intersurgical CC catalogue
9 | NR2 | Directional non-return valve 22M,22M | Intersurgical | 1950 | Intersurgical |  |  | 0.90 | 0.99 | Page 55 in Intersurgical CC catalogue
17 | PSU | External power supply, 13.5v, 4A (50W) | t.b.d. | t.b.d. | RS components | https://uk.rs-online.com/web/p/desktop-power-supplies/7649113/ | RS 764-9113 | 86.39 | 95.03 | Rather expensive, over-specified solution. Find alternative
18 | BATT | Sealed Lead Acid, 12v, 2.1Ahr | Yuasa | NP2.1-12 | RS components | https://uk.rs-online.com/web/p/lead-acid-batteries/0597813 | RS 597-813 | 14.49 | 15.94
20 | PZS | Continuous Piezo Buzzer | t.b.d. | t.b.d. | RS components | https://uk.rs-online.com/web/p/piezo-buzzer-components/6173097/ | RS 617-3097 | 2.63 | 2.89
20 | PZS | Continuous Piezo Buzzer | t.b.d. | t.b.d. | RS components | https://uk.rs-online.com/web/p/piezo-buzzer-components/6173097/ | RS 617-3097 | 2.63 | 2.89
24 | TB1 | Air Hose Clear Polyurethane 8mm OD, 2m length | RS components | RS 917-2404 | RS components | https://uk.rs-online.com/web/p/air-hose/9172400/ | RS 917-2404 | 2.93 | 3.22 | Available in 30m length
25 | TB2 | Air Hose Clear Polyurethane 6mm OD, about 30cm length | RS components | RS 917-2400 | RS components | https://uk.rs-online.com/web/p/air-hose/9172400/ | RS 917-2400 | 0.28 | 0.31
26 | TB3 | Air Hose Clear Polyurethane 6mm OD, about 30cm length | RS components | RS 917-2407 | RS components | https://uk.rs-online.com/web/p/air-hose/9172407/ | RS 917-2407 | 0.20 | 0.22
27 | CN1 | Elbow 22F, 6mm, 22M | Intersurgical | 1893 |  |  |  | 0.50 | 0.55 | Page 9 in Intersurgical AM catalogue
28 | CN2 | Elbow 22M, 22F | Intersurgical | 1992 |  |  |  | 0.50 | 0.55 | Page 9 in Intersurgical AM catalogue
29 | CN3 | T-piece 22M, 6mm, 22F | Intersurgical | 1963 |  |  |  | 0.65 | 0.72 | Page 53 in Intersurgical CC catalogue
30 | CN4 | Straight connector, 8mm to 1/4 thread | RS components | RS 916-0729 | RS components | https://uk.rs-online.com/web/p/pneumatic-straight-fittings/9160729/ | RS 916-0729 | 1.39 | 1.53
31 | CN5 | Elbow connector, 6mm to 1/4 | RS components | RS 176-1404 | RS components | https://uk.rs-online.com/web/p/pneumatic-straight-fittings/1761404/ | RS 176-1404 | 1.60 | 1.76
32 | CN6 | Elbow connector, 6mm to 1/8 | RS components | RS 916-0858 | RS components | https://uk.rs-online.com/web/p/pneumatic-elbow-fittings/9160858/ | RS 916-0858 | 1.96 | 2.16 | 1/4 or whatever the valve port is
33 | CN7 | Elbow connector, 6mm to 1/8 | RS components | RS 916-0858 | RS components | https://uk.rs-online.com/web/p/pneumatic-elbow-fittings/9160858/ | RS 916-0858 | 1.96 | 2.16 | 1/4 or whatever the valve port is
34 | CN8 | T-connector, 6mm, 6mm, 1/8 | RS components | RS 916-0808 | RS components | https://uk.rs-online.com/web/p/pneumatic-t-fittings/9160808/ | RS 916-0808 | 1.78 | 1.96 | 1/4 or whatever the valve port is
35 | CN9 | Elbow connector, 6mm to 1/8 | RS components | RS 916-0858 | RS components | https://uk.rs-online.com/web/p/pneumatic-elbow-fittings/9160858/ | RS 916-0858 | 1.96 | 2.16 | 1/4 or whatever the valve port is
36 | CN10 | T-connector 6mm, 4mm, 6mm | RS components | RS 176-1376 | RS components | https://uk.rs-online.com/web/p/pneumatic-tee-tube-to-tube-adaptors/1761376/ | RS 176-1376 | 2.59 | 2.85
37 | CN11 | Elbow connector, 6mm to 1/8 | RS components | RS 916-0858 | RS components | https://uk.rs-online.com/web/p/pneumatic-elbow-fittings/9160858/ | RS 916-0858 | 1.96 | 2.16 | 1/4 or whatever the valve port is
38 | CN12 | Elbow connector, 6mm to 1/8 | RS components | RS 916-0858 | RS components | https://uk.rs-online.com/web/p/pneumatic-elbow-fittings/9160858/ | RS 916-0858 | 1.96 | 2.16 | 1/4 or whatever the valve port is
39 | CN13 | Elbow connector, 6mm to 1/8 | RS components | RS 916-0858 | RS components | https://uk.rs-online.com/web/p/pneumatic-elbow-fittings/9160858/ | RS 916-0858 | 1.96 | 2.16 | 1/4 or whatever the valve port is
40 | CN14 | Elbow connector, 6mm to 1/8 | RS components | RS 916-0858 | RS components | https://uk.rs-online.com/web/p/pneumatic-elbow-fittings/9160858/ | RS 916-0858 | 1.96 | 2.16 | 1/4 or whatever the valve port is
41 | CN15 | Pneumatic Quick Connect Coupling Brass 1/4 | RS components | RS 667-1730 | RS components | https://uk.rs-online.com/web/p/pneumatic-quick-connect-couplings/6671730/ | RS 667-1730 | 1.75 | 1.93 | 1/4 or whatever the valve port is
42 | ENC | Metal case 280 x 210 x 106 | t.b.d. | t.b.d. | RS components | https://uk.rs-online.com/web/p/instrument-cases/7694902/ | RS 769-4902 | 84.53 | 92.98 | Aluminium Project Box, Black, 350 x 250 x 110mm. Also see RS 818-621,
 |  |  |  |  |  |  |  | 316.49 | 348.14

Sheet: PCB
Source: | /Users/carlospardo/MPLABXProjects/OpenRespirator/Doc/PCB/Main_Board_v1/Main_Board_v1.sch
Date: | Sunday, 26 April 2020 at 17:55:36
Tool: | Eeschema (5.1.5-0-10_14)
Generator: | /private/var/folders/56/xc3q4xws1yb9l04kwy75gbm80000gn/T/AppTranslocation/9ED41D3F-44F4-44D8-B0F9-F94F4ED8C52E/d/kicad.app/Contents/SharedSupport/plugins/bom_csv_grouped_by_value.py
Component Count: | 122
Individual Components:
Item | Qty | Reference(s) | Value | LibPart | Footprint | Datasheet
 |  | C1 | 100nF - 100V | Device:C | Capacitor_THT:C_Rect_L7.2mm_W2.5mm_P5.00mm_FKS2_FKP2_MKS2_MKP2 | https://es.rs-online.com/web/p/condensadores-de-pelicula-de-poliester/1710743/
 |  | C2 | 1uF | Device:C | Capacitor_THT:C_Rect_L13.0mm_W4.0mm_P10.00mm_FKS3_FKP3_MKS4 | https://es.rs-online.com/web/p/condensadores-de-pelicula-de-poliester/1710733/~
 |  | C3 | 1uF | Device:C | Capacitor_THT:C_Rect_L13.0mm_W4.0mm_P10.00mm_FKS3_FKP3_MKS4 | https://es.rs-online.com/web/p/condensadores-de-pelicula-de-poliester/1710733/~
 |  | C4 | 1uF | Device:C | Capacitor_THT:C_Rect_L13.0mm_W4.0mm_P10.00mm_FKS3_FKP3_MKS4 | https://es.rs-online.com/web/p/condensadores-de-pelicula-de-poliester/1710733/~
 |  | C5 | 4.7uF 50V | Device:C | Capacitor_THT:CP_Radial_D5.0mm_P2.00mm | https://es.rs-online.com/web/p/condensadores-de-aluminio/1701286/
 |  | C6 | 1uF | Device:C | Capacitor_THT:C_Rect_L13.0mm_W4.0mm_P10.00mm_FKS3_FKP3_MKS4 | https://es.rs-online.com/web/p/condensadores-de-pelicula-de-poliester/1710733/~
 |  | C7 | 100nF - 100V | Device:C | Capacitor_THT:C_Rect_L7.2mm_W2.5mm_P5.00mm_FKS2_FKP2_MKS2_MKP2 | https://es.rs-online.com/web/p/condensadores-de-pelicula-de-poliester/1710743/
 |  | C8 | 100nF - 100V | Device:C | Capacitor_THT:C_Rect_L7.2mm_W2.5mm_P5.00mm_FKS2_FKP2_MKS2_MKP2 | https://es.rs-online.com/web/p/condensadores-de-pelicula-de-poliester/1710743/
 |  | C9 | 100nF - 100V | Device:C | Capacitor_THT:C_Rect_L7.2mm_W2.5mm_P5.00mm_FKS2_FKP2_MKS2_MKP2 | https://es.rs-online.com/web/p/condensadores-de-pelicula-de-poliester/1710743/
 |  | C10 | 1uF | Device:C | Capacitor_THT:C_Rect_L13.0mm_W4.0mm_P10.00mm_FKS3_FKP3_MKS4 | https://es.rs-online.com/web/p/condensadores-de-pelicula-de-poliester/1710733/~
 |  | C11 | 100nF - 100V | Device:C | Capacitor_THT:C_Rect_L7.2mm_W2.5mm_P5.00mm_FKS2_FKP2_MKS2_MKP2 | https://es.rs-online.com/web/p/condensadores-de-pelicula-de-poliester/1710743/
 |  | C12 | 100nF - 100V | Device:C | Capacitor_THT:C_Rect_L7.2mm_W2.5mm_P5.00mm_FKS2_FKP2_MKS2_MKP2 | https://es.rs-online.com/web/p/condensadores-de-pelicula-de-poliester/1710743/
 |  | C13 | 100nF - 100V | Device:C | Capacitor_THT:C_Rect_L7.2mm_W2.5mm_P5.00mm_FKS2_FKP2_MKS2_MKP2 | https://es.rs-online.com/web/p/condensadores-de-pelicula-de-poliester/1710743/
 |  | C14 | 100nF - 100V | Device:C | Capacitor_THT:C_Rect_L7.2mm_W2.5mm_P5.00mm_FKS2_FKP2_MKS2_MKP2 | https://es.rs-online.com/web/p/condensadores-de-pelicula-de-poliester/1710743/
 |  | C15 | 4.7uF 50V | Device:C | Capacitor_THT:CP_Radial_D5.0mm_P2.00mm | https://es.rs-online.com/web/p/condensadores-de-aluminio/1701286/
 |  | C16 | 100nF - 100V | Device:C | Capacitor_THT:C_Rect_L7.2mm_W2.5mm_P5.00mm_FKS2_FKP2_MKS2_MKP2 | https://es.rs-online.com/web/p/condensadores-de-pelicula-de-poliester/1710743/
 |  | C17 | 100nF - 100V | Device:C | Capacitor_THT:C_Rect_L7.2mm_W2.5mm_P5.00mm_FKS2_FKP2_MKS2_MKP2 | https://es.rs-online.com/web/p/condensadores-de-pelicula-de-poliester/1710743/
 |  | C18 | 1uF | Device:C | Capacitor_THT:C_Rect_L13.0mm_W4.0mm_P10.00mm_FKS3_FKP3_MKS4 | https://es.rs-online.com/web/p/condensadores-de-pelicula-de-poliester/1710733/~
 |  | C19 | 100nF - 100V | Device:C | Capacitor_THT:C_Rect_L7.2mm_W2.5mm_P5.00mm_FKS2_FKP2_MKS2_MKP2 | https://es.rs-online.com/web/p/condensadores-de-pelicula-de-poliester/1710743/
 |  | C20 | 1uF | Device:C | Capacitor_THT:C_Rect_L13.0mm_W4.0mm_P10.00mm_FKS3_FKP3_MKS4 | https://es.rs-online.com/web/p/condensadores-de-pelicula-de-poliester/1710733/~
 |  | C21 | 100nF - 100V | Device:C | Capacitor_THT:C_Rect_L7.2mm_W2.5mm_P5.00mm_FKS2_FKP2_MKS2_MKP2 | https://es.rs-online.com/web/p/condensadores-de-pelicula-de-poliester/1710743/
 |  | C22 | 1uF | Device:C | Capacitor_THT:C_Rect_L13.0mm_W4.0mm_P10.00mm_FKS3_FKP3_MKS4 | https://es.rs-online.com/web/p/condensadores-de-pelicula-de-poliester/1710733/~
 |  | C23 | 1uF | Device:C | Capacitor_THT:C_Rect_L13.0mm_W4.0mm_P10.00mm_FKS3_FKP3_MKS4 | https://es.rs-online.com/web/p/condensadores-de-pelicula-de-poliester/1710733/~
 |  | C24 | 1uF | Device:C | Capacitor_THT:C_Rect_L13.0mm_W4.0mm_P10.00mm_FKS3_FKP3_MKS4 | https://es.rs-online.com/web/p/condensadores-de-pelicula-de-poliester/1710733/~
 |  | C25 | 1uF | Device:C | Capacitor_THT:C_Rect_L13.0mm_W4.0mm_P10.00mm_FKS3_FKP3_MKS4 | https://es.rs-online.com/web/p/condensadores-de-pelicula-de-poliester/1710733/~
 |  | C26 | 1uF | Device:C | Capacitor_THT:C_Rect_L13.0mm_W4.0mm_P10.00mm_FKS3_FKP3_MKS4 | https://es.rs-online.com/web/p/condensadores-de-pelicula-de-poliester/1710733/~
 |  | C27 | 1uF | Device:C | Capacitor_THT:C_Rect_L13.0mm_W4.0mm_P10.00mm_FKS3_FKP3_MKS4 | https://es.rs-online.com/web/p/condensadores-de-pelicula-de-poliester/1710733/~
 |  | C28 | 100nF - 100V | Device:C | Capacitor_THT:C_Rect_L7.2mm_W2.5mm_P5.00mm_FKS2_FKP2_MKS2_MKP2 | https://es.rs-online.com/web/p/condensadores-de-pelicula-de-poliester/1710743/
 |  | C29 | 100nF - 100V | Device:C | Capacitor_THT:C_Rect_L7.2mm_W2.5mm_P5.00mm_FKS2_FKP2_MKS2_MKP2 | https://es.rs-online.com/web/p/condensadores-de-pelicula-de-poliester/1710743/
 |  | C30 | 100nF - 100V | Device:C | Capacitor_THT:C_Rect_L7.2mm_W2.5mm_P5.00mm_FKS2_FKP2_MKS2_MKP2 | https://es.rs-online.com/web/p/condensadores-de-pelicula-de-poliester/1710743/
 |  | D1 | 1N4007 | Diode:1N4001 | Diode_THT:D_DO-41_SOD81_P10.16mm_Horizontal | https://es.rs-online.com/web/p/diodos-schottky-y-rectificadores/6491187/
 |  | D2 | 1N4007 | Diode:1N4001 | Diode_THT:D_DO-41_SOD81_P10.16mm_Horizontal | https://es.rs-online.com/web/p/diodos-schottky-y-rectificadores/6491187/
 |  | D3 | 1N4007 | Diode:1N4001 | Diode_THT:D_DO-41_SOD81_P10.16mm_Horizontal | https://es.rs-online.com/web/p/diodos-schottky-y-rectificadores/6491187/
 |  | D4 | 1N4007 | Diode:1N4001 | Diode_THT:D_DO-41_SOD81_P10.16mm_Horizontal | https://es.rs-online.com/web/p/diodos-schottky-y-rectificadores/6491187/
 |  | J1 | TE_3.5mm_Screwless_P2 | Ventilator:TE_3.5mm_Screwless_P2 | Ventilator:PinHeader_1x02_Screwless_3.5mm | https://es.rs-online.com/web/p/bloques-terminales-para-pcb/1232052/
 |  | J2 | TE_3.5mm_Screwless_P2 | Ventilator:TE_3.5mm_Screwless_P2 | Ventilator:PinHeader_1x02_Screwless_3.5mm | https://es.rs-online.com/web/p/bloques-terminales-para-pcb/1232052/
 |  | J3 | UART_M | Connector:Conn_01x03_Male | Connector_PinHeader_2.54mm:PinHeader_1x03_P2.54mm_Vertical | ~
 |  | J4 | Conn_01x08 | Connector_Generic:Conn_01x08 | Connector_PinHeader_2.54mm:PinHeader_1x08_P2.54mm_Horizontal | ~
 |  | J5 | BUZZER | Connector_Generic:Conn_01x02 | Ventilator:PH_2_pol | https://es.rs-online.com/web/p/componentes-de-piezo-buzzer/6173097/?searchHistory=%7B%22enabled%22%3Atrue%7D
 |  | J6 | I2C Interface LCD_M | Connector:Conn_01x04_Male | Ventilator:PH_4_pol | ~
 |  | J7 | TE_3.5mm_Screwless_P2 | Ventilator:TE_3.5mm_Screwless_P2 | Ventilator:PinHeader_1x02_Screwless_3.5mm | https://es.rs-online.com/web/p/bloques-terminales-para-pcb/1232052/
 |  | J8 | SV2 | Ventilator:TE_3.5mm_Screwless_P2 | Ventilator:PinHeader_1x02_Screwless_3.5mm | https://es.rs-online.com/web/p/bloques-terminales-para-pcb/1232052/
 |  | J9 | SV3 | Ventilator:TE_3.5mm_Screwless_P2 | Ventilator:PinHeader_1x02_Screwless_3.5mm | https://es.rs-online.com/web/p/bloques-terminales-para-pcb/1232052/
 |  | J10 | BPM | Ventilator:Button | Ventilator:PushButton | https://es.rs-online.com/web/p/botones-pulsadores/7346827/
 |  | J11 | UART | Connector:Conn_01x03_Male | Connector_PinHeader_2.54mm:PinHeader_1x03_P2.54mm_Vertical | ~
 |  | J12 | I2C Interface LCD_C | Connector:Conn_01x04_Male | Ventilator:PH_4_pol | ~
 |  | J13 | BUZZER_C | Connector:Conn_01x02_Male | Connector_PinHeader_2.54mm:PinHeader_1x02_P2.54mm_Vertical | https://es.rs-online.com/web/p/componentes-de-piezo-buzzer/6173097/?searchHistory=%7B%22enabled%22%3Atrue%7D
 |  | J14 | MUTE | Ventilator:Button_LED | Ventilator:PushButton_LED | https://es.rs-online.com/web/p/botones-pulsadores/8207521/
 |  | J15 | HISTORY | Ventilator:Button | Ventilator:PushButton | https://es.rs-online.com/web/p/botones-pulsadores/7346827/
 |  | J16 | IP | Ventilator:Button | Ventilator:PushButton | https://es.rs-online.com/web/p/botones-pulsadores/7346827/
 |  | J17 | - | Ventilator:Button | Ventilator:PushButton | https://es.rs-online.com/web/p/botones-pulsadores/7346827/
 |  | J18 | BREATH | Ventilator:Button_LED | Ventilator:PushButton_LED | https://es.rs-online.com/web/p/botones-pulsadores/8207533/
 |  | J19 | EP | Ventilator:Button | Ventilator:PushButton | https://es.rs-online.com/web/p/botones-pulsadores/7346827/
 |  | J20 | + | Ventilator:Button | Ventilator:PushButton | https://es.rs-online.com/web/p/botones-pulsadores/7346827/
 |  | J21 | VOL_MIN | Ventilator:Button | Ventilator:PushButton | https://es.rs-online.com/web/p/botones-pulsadores/7346827/
 |  | J22 | VOL | Ventilator:Button | Ventilator:PushButton | https://es.rs-online.com/web/p/botones-pulsadores/7346827/
 |  | J23 | VOL_MAX | Ventilator:Button | Ventilator:PushButton | https://es.rs-online.com/web/p/botones-pulsadores/7346827/
 |  | J24 | Conn_01x08 | Connector_Generic:Conn_01x08 | Connector_PinHeader_2.54mm:PinHeader_1x08_P2.54mm_Horizontal | ~
 |  | J25 | POWEROFF | Ventilator:Button | Ventilator:PushButton | https://es.rs-online.com/web/p/botones-pulsadores/7346827/
 |  | J26 | PMAX | Ventilator:Button | Ventilator:PushButton | https://es.rs-online.com/web/p/botones-pulsadores/7346827/
 |  | MK1 | Microphone | Device:Microphone | Ventilator:MIC | https://es.rs-online.com/web/p/componentes-de-microfono-para-condensador/7243125/?searchHistory=%7B%22enabled%22%3Atrue%7D
 |  | Q1 | STP24NF10 | Transistor_FET:IRLZ34N | Package_TO_SOT_THT:TO-220-3_Vertical | https://es.rs-online.com/web/p/mosfet/6875377/
 |  | Q2 | STP24NF10 | Transistor_FET:IRLZ34N | Package_TO_SOT_THT:TO-220-3_Vertical | https://es.rs-online.com/web/p/mosfet/6875377/
 |  | Q3 | STP24NF10 | Transistor_FET:IRLZ34N | Package_TO_SOT_THT:TO-220-3_Vertical | https://es.rs-online.com/web/p/mosfet/6875377/
 |  | Q4 | 2N3904 | Transistor_BJT:2N3904 | Ventilator:TO-92_Inline_Ventilator | https://es.rs-online.com/web/p/transistores-bipolares-y-bjt/8051056/
 |  | Q5 | 2N3904 | Transistor_BJT:2N3904 | Ventilator:TO-92_Inline_Ventilator | https://es.rs-online.com/web/p/transistores-bipolares-y-bjt/8051056/
 |  | R1 | 470 | Device:R | Resistor_THT:R_Axial_DIN0207_L6.3mm_D2.5mm_P10.16mm_Horizontal | ~
 |  | R2 | 10k | Device:R | Resistor_THT:R_Axial_DIN0207_L6.3mm_D2.5mm_P10.16mm_Horizontal | ~
 |  | R3 | 220k | Device:R | Resistor_THT:R_Axial_DIN0207_L6.3mm_D2.5mm_P10.16mm_Horizontal | ~
 |  | R4 | 10k | Device:R | Resistor_THT:R_Axial_DIN0207_L6.3mm_D2.5mm_P10.16mm_Horizontal | ~
 |  | R5 | 220k | Device:R | Resistor_THT:R_Axial_DIN0207_L6.3mm_D2.5mm_P10.16mm_Horizontal | ~
 |  | R6 | 1k | Device:R | Resistor_THT:R_Axial_DIN0207_L6.3mm_D2.5mm_P10.16mm_Horizontal | ~
 |  | R7 | 470 | Device:R | Resistor_THT:R_Axial_DIN0207_L6.3mm_D2.5mm_P10.16mm_Horizontal | ~
 |  | R8 | 470 | Device:R | Resistor_THT:R_Axial_DIN0207_L6.3mm_D2.5mm_P10.16mm_Horizontal | ~
 |  | R9 | 10k | Device:R | Resistor_THT:R_Axial_DIN0207_L6.3mm_D2.5mm_P10.16mm_Horizontal | ~
 |  | R10 | 470 | Device:R | Resistor_THT:R_Axial_DIN0207_L6.3mm_D2.5mm_P10.16mm_Horizontal | ~
 |  | R11 | 10k | Device:R | Resistor_THT:R_Axial_DIN0207_L6.3mm_D2.5mm_P10.16mm_Horizontal | ~
 |  | R12 | 470 | Device:R | Resistor_THT:R_Axial_DIN0207_L6.3mm_D2.5mm_P10.16mm_Horizontal | ~
 |  | R13 | 470 | Device:R | Resistor_THT:R_Axial_DIN0207_L6.3mm_D2.5mm_P10.16mm_Horizontal | ~
 |  | R14 | 1k | Device:R | Resistor_THT:R_Axial_DIN0207_L6.3mm_D2.5mm_P10.16mm_Horizontal | ~
 |  | R15 | 470 | Device:R | Resistor_THT:R_Axial_DIN0207_L6.3mm_D2.5mm_P10.16mm_Horizontal | ~
 |  | R16 | 470 | Device:R | Resistor_THT:R_Axial_DIN0207_L6.3mm_D2.5mm_P10.16mm_Horizontal | ~
 |  | R17 | 470 | Device:R | Resistor_THT:R_Axial_DIN0207_L6.3mm_D2.5mm_P10.16mm_Horizontal | ~
 |  | R18 | 10k | Device:R | Resistor_THT:R_Axial_DIN0207_L6.3mm_D2.5mm_P10.16mm_Horizontal | ~
 |  | R19 | 10k | Device:R | Resistor_THT:R_Axial_DIN0207_L6.3mm_D2.5mm_P10.16mm_Horizontal | ~
 |  | R20 | 10k | Device:R | Resistor_THT:R_Axial_DIN0207_L6.3mm_D2.5mm_P10.16mm_Horizontal | ~
 |  | R21 | 10k | Device:R | Resistor_THT:R_Axial_DIN0207_L6.3mm_D2.5mm_P10.16mm_Horizontal | ~
 |  | R22 | 10k | Device:R | Resistor_THT:R_Axial_DIN0207_L6.3mm_D2.5mm_P10.16mm_Horizontal | ~
 |  | R23 | 10k | Device:R | Resistor_THT:R_Axial_DIN0207_L6.3mm_D2.5mm_P10.16mm_Horizontal | ~
 |  | R24 | 2k2 | Device:R | Resistor_THT:R_Axial_DIN0207_L6.3mm_D2.5mm_P10.16mm_Horizontal | ~
 |  | R25 | 1k | Device:R | Resistor_THT:R_Axial_DIN0207_L6.3mm_D2.5mm_P10.16mm_Horizontal | ~
 |  | R26 | 1k | Device:R | Resistor_THT:R_Axial_DIN0207_L6.3mm_D2.5mm_P10.16mm_Horizontal | ~
 |  | R27 | 2k2 | Device:R | Resistor_THT:R_Axial_DIN0207_L6.3mm_D2.5mm_P10.16mm_Horizontal | ~
 |  | R28 | 2k2 | Device:R | Resistor_THT:R_Axial_DIN0207_L6.3mm_D2.5mm_P10.16mm_Horizontal | ~
 |  | R29 | 470 | Device:R | Resistor_THT:R_Axial_DIN0207_L6.3mm_D2.5mm_P10.16mm_Horizontal | ~
 |  | R30 | 10k | Device:R | Resistor_THT:R_Axial_DIN0207_L6.3mm_D2.5mm_P10.16mm_Horizontal | ~
 |  | R31 | 10k | Device:R | Resistor_THT:R_Axial_DIN0207_L6.3mm_D2.5mm_P10.16mm_Horizontal | ~
 |  | R32 | 10k | Device:R | Resistor_THT:R_Axial_DIN0207_L6.3mm_D2.5mm_P10.16mm_Horizontal | ~
 |  | R33 | 470 | Device:R | Resistor_THT:R_Axial_DIN0207_L6.3mm_D2.5mm_P10.16mm_Horizontal | ~
 |  | R34 | 470 | Device:R | Resistor_THT:R_Axial_DIN0207_L6.3mm_D2.5mm_P10.16mm_Horizontal | ~
 |  | R35 | 10k | Device:R | Resistor_THT:R_Axial_DIN0207_L6.3mm_D2.5mm_P10.16mm_Horizontal | ~
 |  | R36 | 10k | Device:R | Resistor_THT:R_Axial_DIN0207_L6.3mm_D2.5mm_P10.16mm_Horizontal | ~
 |  | R37 | 10k | Device:R | Resistor_THT:R_Axial_DIN0207_L6.3mm_D2.5mm_P10.16mm_Horizontal | ~
 |  | R38 | 10k | Device:R | Resistor_THT:R_Axial_DIN0207_L6.3mm_D2.5mm_P10.16mm_Horizontal | ~
 |  | R39 | 470 | Device:R | Resistor_THT:R_Axial_DIN0207_L6.3mm_D2.5mm_P10.16mm_Horizontal | ~
 |  | R40 | 470 | Device:R | Resistor_THT:R_Axial_DIN0207_L6.3mm_D2.5mm_P10.16mm_Horizontal | ~
 |  | R41 | 470 | Device:R | Resistor_THT:R_Axial_DIN0207_L6.3mm_D2.5mm_P10.16mm_Horizontal | ~
 |  | R42 | 470 | Device:R | Resistor_THT:R_Axial_DIN0207_L6.3mm_D2.5mm_P10.16mm_Horizontal | ~
 |  | R43 | 4.7 | Device:R | Resistor_THT:R_Axial_DIN0207_L6.3mm_D2.5mm_P10.16mm_Horizontal | ~
 |  | RV1 | 1K | Device:R_POT | Ventilator:Potentiometer_409HA | https://es.rs-online.com/web/p/resistencias-variables/6524546/
 |  | RV2 | 1K | Device:R_POT | Ventilator:Potentiometer_409HA | https://es.rs-online.com/web/p/resistencias-variables/6524546/
 |  | S1 | MPXV5004DP | Ventilator:MPXV5004DP | Ventilator:1351-01 | https://es.rs-online.com/web/p/sensores-de-presion/9227399/
 |  | S2 | MPXV5010DP | Ventilator:MPXV5010DP | Ventilator:1351-01 | https://es.rs-online.com/web/p/circuitos-integrados-de-sensor-de-presion-diferencial/7191184/
 |  | S3 | MPXV5010DP | Ventilator:MPXV5010DP | Ventilator:1351-01 | https://es.rs-online.com/web/p/circuitos-integrados-de-sensor-de-presion-diferencial/7191184/
 |  | S4 | MPXV5004DP | Ventilator:MPXV5004DP | Ventilator:1351-01 | https://es.rs-online.com/web/p/sensores-de-presion/9227399/
 |  | U1 | LM358 | Amplifier_Operational:LM358 | Package_DIP:DIP-8_W7.62mm_LongPads | https://es.rs-online.com/web/p/amplificadores-operacionales/9216923/
 |  | U2 | LM7805_TO220 | Regulator_Linear:LM7805_TO220 | Package_TO_SOT_THT:TO-220-3_Vertical | https://es.rs-online.com/web/p/reguladores-de-tension-lineal/9222369/
 |  | U3 | XPRESS-40 | Ventilator:XPRESS-40 | Ventilator:EXPRESS-40_DIP_40 | https://es.rs-online.com/web/p/kits-de-desarrollo-de-procesador-y-microcontrolador/1744238/
 |  | U4 | LM7805_TO220 | Regulator_Linear:LM7805_TO220 | Package_TO_SOT_THT:TO-220-3_Vertical | https://es.rs-online.com/web/p/reguladores-de-tension-lineal/9222369/
 |  | U5 | XPRESS-40 | Ventilator:XPRESS-40 | Ventilator:EXPRESS-40_DIP_40 | https://es.rs-online.com/web/p/kits-de-desarrollo-de-procesador-y-microcontrolador/1744238/
 |  | U6 | LCD | Ventilator:LCD | Ventilator:LCD_2x16
 |  | U7 | LCD | Ventilator:LCD | Ventilator:LCD_2x16
Collated Components:
Item | Qty | Reference(s) | Value | LibPart | Footprint | Datasheet
1 | 15 | C1, C7, C8, C9, C11, C12, C13, C14, C16, C17, C19, C21, C28, C29, C30 | 100nF - 100V | Device:C | Capacitor_THT:C_Rect_L7.2mm_W2.5mm_P5.00mm_FKS2_FKP2_MKS2_MKP2 | https://es.rs-online.com/web/p/condensadores-de-pelicula-de-poliester/1710743/
2 | 13 | C2, C3, C4, C6, C10, C18, C20, C22, C23, C24, C25, C26, C27 | 1uF | Device:C | Capacitor_THT:C_Rect_L13.0mm_W4.0mm_P10.00mm_FKS3_FKP3_MKS4 | https://es.rs-online.com/web/p/condensadores-de-pelicula-de-poliester/1710733/~
3 | 2 | C5, C15 | 4.7uF 50V | Device:C | Capacitor_THT:CP_Radial_D5.0mm_P2.00mm | https://es.rs-online.com/web/p/condensadores-de-aluminio/1701286/
4 | 4 | D1, D2, D3, D4 | 1N4007 | Diode:1N4001 | Diode_THT:D_DO-41_SOD81_P10.16mm_Horizontal | https://es.rs-online.com/web/p/diodos-schottky-y-rectificadores/6491187/
5 | 3 | J1, J2, J7 | TE_3.5mm_Screwless_P2 | Ventilator:TE_3.5mm_Screwless_P2 | Ventilator:PinHeader_1x02_Screwless_3.5mm | https://es.rs-online.com/web/p/bloques-terminales-para-pcb/1232052/
6 | 1 | J3 | UART_M | Connector:Conn_01x03_Male | Connector_PinHeader_2.54mm:PinHeader_1x03_P2.54mm_Vertical | ~
7 | 2 | J4, J24 | Conn_01x08 | Connector_Generic:Conn_01x08 | Connector_PinHeader_2.54mm:PinHeader_1x08_P2.54mm_Horizontal | ~
8 | 1 | J5 | BUZZER | Connector_Generic:Conn_01x02 | Ventilator:PH_2_pol | https://es.rs-online.com/web/p/componentes-de-piezo-buzzer/6173097/?searchHistory=%7B%22enabled%22%3Atrue%7D
9 | 1 | J6 | I2C Interface LCD_M | Connector:Conn_01x04_Male | Ventilator:PH_4_pol | ~
10 | 1 | J8 | SV2 | Ventilator:TE_3.5mm_Screwless_P2 | Ventilator:PinHeader_1x02_Screwless_3.5mm | https://es.rs-online.com/web/p/bloques-terminales-para-pcb/1232052/
11 | 1 | J9 | SV3 | Ventilator:TE_3.5mm_Screwless_P2 | Ventilator:PinHeader_1x02_Screwless_3.5mm | https://es.rs-online.com/web/p/bloques-terminales-para-pcb/1232052/
12 | 1 | J10 | BPM | Ventilator:Button | Ventilator:PushButton | https://es.rs-online.com/web/p/botones-pulsadores/7346827/
13 | 1 | J11 | UART | Connector:Conn_01x03_Male | Connector_PinHeader_2.54mm:PinHeader_1x03_P2.54mm_Vertical | ~
14 | 1 | J12 | I2C Interface LCD_C | Connector:Conn_01x04_Male | Ventilator:PH_4_pol | ~
15 | 1 | J13 | BUZZER_C | Connector:Conn_01x02_Male | Connector_PinHeader_2.54mm:PinHeader_1x02_P2.54mm_Vertical | https://es.rs-online.com/web/p/componentes-de-piezo-buzzer/6173097/?searchHistory=%7B%22enabled%22%3Atrue%7D
16 | 1 | J14 | MUTE | Ventilator:Button_LED | Ventilator:PushButton_LED | https://es.rs-online.com/web/p/botones-pulsadores/8207521/
17 | 1 | J15 | HISTORY | Ventilator:Button | Ventilator:PushButton | https://es.rs-online.com/web/p/botones-pulsadores/7346827/
18 | 1 | J16 | IP | Ventilator:Button | Ventilator:PushButton | https://es.rs-online.com/web/p/botones-pulsadores/7346827/
19 | 1 | J17 | - | Ventilator:Button | Ventilator:PushButton | https://es.rs-online.com/web/p/botones-pulsadores/7346827/
20 | 1 | J18 | BREATH | Ventilator:Button_LED | Ventilator:PushButton_LED | https://es.rs-online.com/web/p/botones-pulsadores/8207533/
21 | 1 | J19 | EP | Ventilator:Button | Ventilator:PushButton | https://es.rs-online.com/web/p/botones-pulsadores/7346827/
22 | 1 | J20 | + | Ventilator:Button | Ventilator:PushButton | https://es.rs-online.com/web/p/botones-pulsadores/7346827/
23 | 1 | J21 | VOL_MIN | Ventilator:Button | Ventilator:PushButton | https://es.rs-online.com/web/p/botones-pulsadores/7346827/
24 | 1 | J22 | VOL | Ventilator:Button | Ventilator:PushButton | https://es.rs-online.com/web/p/botones-pulsadores/7346827/
25 | 1 | J23 | VOL_MAX | Ventilator:Button | Ventilator:PushButton | https://es.rs-online.com/web/p/botones-pulsadores/7346827/
26 | 1 | J25 | POWEROFF | Ventilator:Button | Ventilator:PushButton | https://es.rs-online.com/web/p/botones-pulsadores/7346827/
27 | 1 | J26 | PMAX | Ventilator:Button | Ventilator:PushButton | https://es.rs-online.com/web/p/botones-pulsadores/7346827/
28 | 1 | MK1 | Microphone | Device:Microphone | Ventilator:MIC | https://es.rs-online.com/web/p/componentes-de-microfono-para-condensador/7243125/?searchHistory=%7B%22enabled%22%3Atrue%7D
29 | 3 | Q1, Q2, Q3 | STP24NF10 | Transistor_FET:IRLZ34N | Package_TO_SOT_THT:TO-220-3_Vertical | https://es.rs-online.com/web/p/mosfet/6875377/
30 | 2 | Q4, Q5 | 2N3904 | Transistor_BJT:2N3904 | Ventilator:TO-92_Inline_Ventilator | https://es.rs-online.com/web/p/transistores-bipolares-y-bjt/8051056/
31 | 12 | R1, R7, R8, R10, R12, R13, R15, R16, R17, R29, R33, R34 | 470 | Device:R | Resistor_THT:R_Axial_DIN0207_L6.3mm_D2.5mm_P10.16mm_Horizontal | ~
32 | 17 | R2, R4, R9, R11, R18, R19, R20, R21, R22, R23, R30, R31, R32, R35, R36, R37, R38 | 10k | Device:R | Resistor_THT:R_Axial_DIN0207_L6.3mm_D2.5mm_P10.16mm_Horizontal | ~
33 | 2 | R3, R5 | 220k | Device:R | Resistor_THT:R_Axial_DIN0207_L6.3mm_D2.5mm_P10.16mm_Horizontal | ~
34 | 4 | R6, R14, R25, R26 | 1k | Device:R | Resistor_THT:R_Axial_DIN0207_L6.3mm_D2.5mm_P10.16mm_Horizontal | ~
35 | 3 | R24, R27, R28 | 2k2 | Device:R | Resistor_THT:R_Axial_DIN0207_L6.3mm_D2.5mm_P10.16mm_Horizontal | ~
36 | 4 | R39, R40, R41, R42 | 470 | Device:R | Resistor_THT:R_Axial_DIN0207_L6.3mm_D2.5mm_P10.16mm_Horizontal | ~
37 | 1 | R43 | 4.7 | Device:R | Resistor_THT:R_Axial_DIN0207_L6.3mm_D2.5mm_P10.16mm_Horizontal | ~
38 | 2 | RV1, RV2 | 1K | Device:R_POT | Ventilator:Potentiometer_409HA | https://es.rs-online.com/web/p/resistencias-variables/6524546/
39 | 2 | S1, S4 | MPXV5004DP | Ventilator:MPXV5004DP | Ventilator:1351-01 | https://es.rs-online.com/web/p/sensores-de-presion/9227399/
40 | 2 | S2, S3 | MPXV5010DP | Ventilator:MPXV5010DP | Ventilator:1351-01 | https://es.rs-online.com/web/p/circuitos-integrados-de-sensor-de-presion-diferencial/7191184/
41 | 1 | U1 | LM358 | Amplifier_Operational:LM358 | Package_DIP:DIP-8_W7.62mm_LongPads | https://es.rs-online.com/web/p/amplificadores-operacionales/9216923/
42 | 2 | U2, U4 | LM7805_TO220 | Regulator_Linear:LM7805_TO220 | Package_TO_SOT_THT:TO-220-3_Vertical | https://es.rs-online.com/web/p/reguladores-de-tension-lineal/9222369/
43 | 2 | U3, U5 | XPRESS-40 | Ventilator:XPRESS-40 | Ventilator:EXPRESS-40_DIP_40 | https://es.rs-online.com/web/p/kits-de-desarrollo-de-procesador-y-microcontrolador/1744238/
44 | 2 | U6, U7 | LCD | Ventilator:LCD | Ventilator:LCD_2x16

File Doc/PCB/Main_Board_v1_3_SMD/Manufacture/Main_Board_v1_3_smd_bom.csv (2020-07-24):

Source: | /Users/carlospardo/MPLABXProjects/OpenRespirator/Doc/PCB/Main_Board_v1_3_SMD/Main_Board_v1_3_smd.sch
Date: | Wednesday, 08 July 2020 at 15:33:49
Tool: | Eeschema (5.1.5-0-10_14)
Component Count: | 144
Ref | Value | Footprint | Datasheet | Manufacturer | Vendor
C1 | 100nF - 100V | Capacitor_SMD:C_1206_3216Metric_Pad1.42x1.75mm_HandSolder | https://es.rs-online.com/web/p/mlccs-condensadores-ceramicos-multicapa/1700197/
C2 | 1uF | Capacitor_SMD:C_1206_3216Metric_Pad1.42x1.75mm_HandSolder | Capacitor_SMD:C_1206_3216Metric_Pad1.42x1.75mm_HandSolder
C3 | 1uF | Capacitor_SMD:C_1206_3216Metric_Pad1.42x1.75mm_HandSolder | Capacitor_SMD:C_1206_3216Metric_Pad1.42x1.75mm_HandSolder
C4 | 1uF | Capacitor_SMD:C_1206_3216Metric_Pad1.42x1.75mm_HandSolder | Capacitor_SMD:C_1206_3216Metric_Pad1.42x1.75mm_HandSolder
C5 | 4.7uF 50V | Capacitor_THT:CP_Radial_D5.0mm_P2.00mm | https://es.rs-online.com/web/p/condensadores-de-aluminio/1701286/
C6 | 1uF | Capacitor_SMD:C_1206_3216Metric_Pad1.42x1.75mm_HandSolder | Capacitor_SMD:C_1206_3216Metric_Pad1.42x1.75mm_HandSolder
C7 | 100nF - 100V | Capacitor_SMD:C_1206_3216Metric_Pad1.42x1.75mm_HandSolder | https://es.rs-online.com/web/p/mlccs-condensadores-ceramicos-multicapa/1700197/
C8 | 100nF - 100V | Capacitor_SMD:C_1206_3216Metric_Pad1.42x1.75mm_HandSolder | https://es.rs-online.com/web/p/mlccs-condensadores-ceramicos-multicapa/1700197/
C9 | 100nF - 100V | Capacitor_SMD:C_1206_3216Metric_Pad1.42x1.75mm_HandSolder | https://es.rs-online.com/web/p/mlccs-condensadores-ceramicos-multicapa/1700197/
C10 | 1uF | Capacitor_SMD:C_1206_3216Metric_Pad1.42x1.75mm_HandSolder | Capacitor_SMD:C_1206_3216Metric_Pad1.42x1.75mm_HandSolder
C11 | 100nF - 100V | Capacitor_SMD:C_1206_3216Metric_Pad1.42x1.75mm_HandSolder | https://es.rs-online.com/web/p/mlccs-condensadores-ceramicos-multicapa/1700197/
C12 | 100nF - 100V | Capacitor_SMD:C_1206_3216Metric_Pad1.42x1.75mm_HandSolder | https://es.rs-online.com/web/p/mlccs-condensadores-ceramicos-multicapa/1700197/
C13 | 100nF - 100V | Capacitor_SMD:C_1206_3216Metric_Pad1.42x1.75mm_HandSolder | https://es.rs-online.com/web/p/mlccs-condensadores-ceramicos-multicapa/1700197/
C14 | 100nF - 100V | Capacitor_SMD:C_1206_3216Metric_Pad1.42x1.75mm_HandSolder | https://es.rs-online.com/web/p/mlccs-condensadores-ceramicos-multicapa/1700197/
C15 | 4.7uF 50V | Capacitor_THT:CP_Radial_D5.0mm_P2.00mm | https://es.rs-online.com/web/p/condensadores-de-aluminio/1701286/
C16 | 100nF - 100V | Capacitor_SMD:C_1206_3216Metric_Pad1.42x1.75mm_HandSolder | https://es.rs-online.com/web/p/mlccs-condensadores-ceramicos-multicapa/1700197/
C17 | 100nF - 100V | Capacitor_SMD:C_1206_3216Metric_Pad1.42x1.75mm_HandSolder | https://es.rs-online.com/web/p/mlccs-condensadores-ceramicos-multicapa/1700197/
C18 | 1uF | Capacitor_SMD:C_1206_3216Metric_Pad1.42x1.75mm_HandSolder | Capacitor_SMD:C_1206_3216Metric_Pad1.42x1.75mm_HandSolder
C19 | 100nF - 100V | Capacitor_SMD:C_1206_3216Metric_Pad1.42x1.75mm_HandSolder | https://es.rs-online.com/web/p/mlccs-condensadores-ceramicos-multicapa/1700197/
C20 | 1uF | Capacitor_SMD:C_1206_3216Metric_Pad1.42x1.75mm_HandSolder | Capacitor_SMD:C_1206_3216Metric_Pad1.42x1.75mm_HandSolder
C21 | 100nF - 100V | Capacitor_SMD:C_1206_3216Metric_Pad1.42x1.75mm_HandSolder | https://es.rs-online.com/web/p/mlccs-condensadores-ceramicos-multicapa/1700197/
C22 | 1uF | Capacitor_SMD:C_1206_3216Metric_Pad1.42x1.75mm_HandSolder | Capacitor_SMD:C_1206_3216Metric_Pad1.42x1.75mm_HandSolder
C23 | 1uF | Capacitor_SMD:C_1206_3216Metric_Pad1.42x1.75mm_HandSolder | Capacitor_SMD:C_1206_3216Metric_Pad1.42x1.75mm_HandSolder
C24 | 1uF | Capacitor_SMD:C_1206_3216Metric_Pad1.42x1.75mm_HandSolder | Capacitor_SMD:C_1206_3216Metric_Pad1.42x1.75mm_HandSolder
C25 | 1uF | Capacitor_SMD:C_1206_3216Metric_Pad1.42x1.75mm_HandSolder | Capacitor_SMD:C_1206_3216Metric_Pad1.42x1.75mm_HandSolder
C26 | 1uF | Capacitor_SMD:C_1206_3216Metric_Pad1.42x1.75mm_HandSolder | Capacitor_SMD:C_1206_3216Metric_Pad1.42x1.75mm_HandSolder
C27 | 1uF | Capacitor_SMD:C_1206_3216Metric_Pad1.42x1.75mm_HandSolder | Capacitor_SMD:C_1206_3216Metric_Pad1.42x1.75mm_HandSolder
C28 | 100nF - 100V | Capacitor_SMD:C_1206_3216Metric_Pad1.42x1.75mm_HandSolder | https://es.rs-online.com/web/p/mlccs-condensadores-ceramicos-multicapa/1700197/
C29 | 100nF - 100V | Capacitor_SMD:C_1206_3216Metric_Pad1.42x1.75mm_HandSolder | https://es.rs-online.com/web/p/mlccs-condensadores-ceramicos-multicapa/1700197/
C30 | 100nF - 100V | Capacitor_SMD:C_1206_3216Metric_Pad1.42x1.75mm_HandSolder | https://es.rs-online.com/web/p/mlccs-condensadores-ceramicos-multicapa/1700197/
C31 | 1uF | Capacitor_SMD:C_1206_3216Metric_Pad1.42x1.75mm_HandSolder | Capacitor_SMD:C_1206_3216Metric_Pad1.42x1.75mm_HandSolder
C32 | 1uF | Capacitor_SMD:C_1206_3216Metric_Pad1.42x1.75mm_HandSolder | Capacitor_SMD:C_1206_3216Metric_Pad1.42x1.75mm_HandSolder
C33 | 1uF | Capacitor_SMD:C_1206_3216Metric_Pad1.42x1.75mm_HandSolder | Capacitor_SMD:C_1206_3216Metric_Pad1.42x1.75mm_HandSolder
D1 | 1A - 100V | Diode_SMD:D_SMA-SMB_Universal_Handsoldering | https://es.rs-online.com/web/p/diodo-de-conmutacion/1221183/
D2 | 1A - 100V | Diode_SMD:D_SMA-SMB_Universal_Handsoldering | https://es.rs-online.com/web/p/diodo-de-conmutacion/1221183/
D3 | 1A - 100V | Diode_SMD:D_SMA-SMB_Universal_Handsoldering | https://es.rs-online.com/web/p/diodo-de-conmutacion/1221183/
D4 | 1A - 100V | Diode_SMD:D_SMA-SMB_Universal_Handsoldering | https://es.rs-online.com/web/p/diodo-de-conmutacion/1221183/
D5 | ALARM | LED_THT:LED_D3.0mm | ~
D6 | BREATH | LED_THT:LED_D3.0mm | ~
D7 | 1A - 100V | Diode_SMD:D_SMA-SMB_Universal_Handsoldering | https://es.rs-online.com/web/p/diodo-de-conmutacion/1221183/
F1 | FIDU | Ventilator:FIDUCIAL_TEST_PCB_1C
F2 | FIDU | Ventilator:FIDUCIAL_TEST_PCB_1C
F3 | FIDU | Ventilator:FIDUCIAL_TEST_PCB_1C
F4 | FIDU | Ventilator:FIDUCIAL_TEST_PCB_1C
F5 | FIDU | Ventilator:FIDUCIAL_TEST_PCB_1C
F6 | FIDU | Ventilator:FIDUCIAL_TEST_PCB_1C
F7 | FIDU | Ventilator:FIDUCIAL_TEST_PCB_1C
F8 | FIDU | Ventilator:FIDUCIAL_TEST_PCB_1C
J1 | SV1 | Ventilator:PinHeader_1x02_Screwless_3.5mm | https://es.rs-online.com/web/p/bloques-terminales-para-pcb/1232052/
J2 | 12V | Ventilator:PinHeader_1x02_Screwless_3.5mm | https://es.rs-online.com/web/p/bloques-terminales-para-pcb/1232052/
J3 | UART_M | Connector_PinHeader_2.54mm:PinHeader_1x03_P2.54mm_Vertical | ~
J4 | Conn_01x05 | Connector_PinHeader_2.54mm:PinHeader_1x05_P2.54mm_Horizontal | ~
J5 | BUZZER_M | Ventilator:PH_2_pol | https://es.rs-online.com/web/p/componentes-de-piezo-buzzer/6173097/?searchHistory=%7B%22enabled%22%3Atrue%7D
J6 | I2C Interface LCD_M | Ventilator:PH_4_pol | ~
J7 | 12V | Ventilator:PinHeader_1x02_Screwless_3.5mm | https://es.rs-online.com/web/p/bloques-terminales-para-pcb/1232052/
J8 | SV2 | Ventilator:PinHeader_1x02_Screwless_3.5mm | https://es.rs-online.com/web/p/bloques-terminales-para-pcb/1232052/
J9 | SV3 | Ventilator:PinHeader_1x02_Screwless_3.5mm | https://es.rs-online.com/web/p/bloques-terminales-para-pcb/1232052/
J11 | UART | Connector_PinHeader_2.54mm:PinHeader_1x03_P2.54mm_Vertical | ~
J12 | I2C Interface LCD_C | Ventilator:PH_4_pol | ~
J13 | BUZZER_C | Connector_PinHeader_2.54mm:PinHeader_1x02_P2.54mm_Vertical | https://es.rs-online.com/web/p/componentes-de-piezo-buzzer/6173097/?searchHistory=%7B%22enabled%22%3Atrue%7D
J24 | Conn_01x06 | Connector_PinHeader_2.54mm:PinHeader_1x06_P2.54mm_Horizontal | ~
J25 | POWEROFF | Ventilator:PH_2_pol
J27 | SV4 | Ventilator:PinHeader_1x02_Screwless_3.5mm | https://es.rs-online.com/web/p/bloques-terminales-para-pcb/1232052/
MK1 | Microphone | Ventilator:MIC | https://es.rs-online.com/web/p/componentes-de-microfono-para-condensador/7243125/?searchHistory=%7B%22enabled%22%3Atrue%7D
Q1 | FDT1600N10ALZ | Package_TO_SOT_SMD:SOT-223-3_TabPin2 | https://es.rs-online.com/web/p/mosfet/1662305/
Q2 | FDT1600N10ALZ | Package_TO_SOT_SMD:SOT-223-3_TabPin2 | https://es.rs-online.com/web/p/mosfet/1662305/
Q3 | FDT1600N10ALZ | Package_TO_SOT_SMD:SOT-223-3_TabPin2 | https://es.rs-online.com/web/p/mosfet/1662305/
Q4 | BSR19A | Package_TO_SOT_SMD:SOT-23 | https://es.rs-online.com/web/p/transistores-bipolares-y-bjt/1821856/
Q5 | BSR19A | Package_TO_SOT_SMD:SOT-23 | https://es.rs-online.com/web/p/transistores-bipolares-y-bjt/1821856/
Q6 | FDT1600N10ALZ | Package_TO_SOT_SMD:SOT-223-3_TabPin2 | https://es.rs-online.com/web/p/mosfet/1662305/
R1 | 470 | Resistor_SMD:R_0603_1608Metric_Pad1.05x0.95mm_HandSolder | ~
R2 | 10k | Resistor_SMD:R_0603_1608Metric_Pad1.05x0.95mm_HandSolder | ~
R3 | 220k | Resistor_SMD:R_0603_1608Metric_Pad1.05x0.95mm_HandSolder | ~
R4 | 10k | Resistor_SMD:R_0603_1608Metric_Pad1.05x0.95mm_HandSolder | ~
R5 | 220k | Resistor_SMD:R_0603_1608Metric_Pad1.05x0.95mm_HandSolder | ~
R6 | 1k | Resistor_SMD:R_0603_1608Metric_Pad1.05x0.95mm_HandSolder | ~
R7 | 470 | Resistor_SMD:R_0603_1608Metric_Pad1.05x0.95mm_HandSolder | ~
R8 | 470 | Resistor_SMD:R_0603_1608Metric_Pad1.05x0.95mm_HandSolder | ~
R9 | 10k | Resistor_SMD:R_0603_1608Metric_Pad1.05x0.95mm_HandSolder | ~
R10 | 470 | Resistor_SMD:R_0603_1608Metric_Pad1.05x0.95mm_HandSolder | ~
R11 | 10k | Resistor_SMD:R_0603_1608Metric_Pad1.05x0.95mm_HandSolder | ~
R12 | 470 | Resistor_SMD:R_0603_1608Metric_Pad1.05x0.95mm_HandSolder | ~
R13 | 470 | Resistor_SMD:R_0603_1608Metric_Pad1.05x0.95mm_HandSolder | ~
R14 | 1k | Resistor_SMD:R_0603_1608Metric_Pad1.05x0.95mm_HandSolder | ~
R15 | 470 | Resistor_SMD:R_0603_1608Metric_Pad1.05x0.95mm_HandSolder | ~
R16 | 470 | Resistor_SMD:R_0603_1608Metric_Pad1.05x0.95mm_HandSolder | ~
R17 | 470 | Resistor_SMD:R_0603_1608Metric_Pad1.05x0.95mm_HandSolder | ~
R18 | 10k | Resistor_SMD:R_0603_1608Metric_Pad1.05x0.95mm_HandSolder | ~
R19 | 10k | Resistor_SMD:R_0603_1608Metric_Pad1.05x0.95mm_HandSolder | ~
R20 | 10k | Resistor_SMD:R_0603_1608Metric_Pad1.05x0.95mm_HandSolder | ~
R21 | 10k | Resistor_SMD:R_0603_1608Metric_Pad1.05x0.95mm_HandSolder | ~
R22 | 10k | Resistor_SMD:R_0603_1608Metric_Pad1.05x0.95mm_HandSolder | ~
R23 | 10k | Resistor_SMD:R_0603_1608Metric_Pad1.05x0.95mm_HandSolder | ~
R24 | 2k2 | Resistor_SMD:R_0603_1608Metric_Pad1.05x0.95mm_HandSolder | ~
R25 | 1k | Resistor_SMD:R_0603_1608Metric_Pad1.05x0.95mm_HandSolder | ~
R26 | 1k | Resistor_SMD:R_0603_1608Metric_Pad1.05x0.95mm_HandSolder | ~
R27 | 2k2 | Resistor_SMD:R_0603_1608Metric_Pad1.05x0.95mm_HandSolder | ~
R28 | 2k2 | Resistor_SMD:R_0603_1608Metric_Pad1.05x0.95mm_HandSolder | ~
R29 | 470 | Resistor_SMD:R_0603_1608Metric_Pad1.05x0.95mm_HandSolder | ~
R30 | 10k | Resistor_SMD:R_0603_1608Metric_Pad1.05x0.95mm_HandSolder | ~
R31 | 10k | Resistor_SMD:R_0603_1608Metric_Pad1.05x0.95mm_HandSolder | ~
R32 | 10k | Resistor_SMD:R_0603_1608Metric_Pad1.05x0.95mm_HandSolder | ~
R33 | 2k2 | Resistor_SMD:R_0603_1608Metric_Pad1.05x0.95mm_HandSolder | ~
R34 | 2k2 | Resistor_SMD:R_0603_1608Metric_Pad1.05x0.95mm_HandSolder | ~
R35 | 10k | Resistor_SMD:R_0603_1608Metric_Pad1.05x0.95mm_HandSolder | ~
R36 | 10k | Resistor_SMD:R_0603_1608Metric_Pad1.05x0.95mm_HandSolder | ~
R37 | 10k | Resistor_SMD:R_0603_1608Metric_Pad1.05x0.95mm_HandSolder | ~
R38 | 10k | Resistor_SMD:R_0603_1608Metric_Pad1.05x0.95mm_HandSolder | ~
R39 | 470 | Resistor_SMD:R_0603_1608Metric_Pad1.05x0.95mm_HandSolder | ~
R40 | 470 | Resistor_SMD:R_0603_1608Metric_Pad1.05x0.95mm_HandSolder | ~
R41 | 470 | Resistor_SMD:R_0603_1608Metric_Pad1.05x0.95mm_HandSolder | ~
R42 | 470 | Resistor_SMD:R_0603_1608Metric_Pad1.05x0.95mm_HandSolder | ~
R43 | 4.7 | Resistor_SMD:R_0603_1608Metric_Pad1.05x0.95mm_HandSolder | ~
R44 | 4.7 | Resistor_SMD:R_0603_1608Metric_Pad1.05x0.95mm_HandSolder | ~
R45 | 1k | Resistor_SMD:R_0603_1608Metric_Pad1.05x0.95mm_HandSolder | ~
RV1 | 5K | Potentiometer_SMD:Potentiometer_Vishay_TS53YJ_Vertical | https://es.rs-online.com/web/p/resistencias-variables/1679441/
RV2 | 5K | Potentiometer_SMD:Potentiometer_Vishay_TS53YJ_Vertical | https://es.rs-online.com/web/p/resistencias-variables/1679441/
S1 | MPXV5004DP | Ventilator:1351-01 | https://es.rs-online.com/web/p/sensores-de-presion/9227399/
S2 | MPXV5010DP | Ventilator:1351-01 | https://es.rs-online.com/web/p/circuitos-integrados-de-sensor-de-presion-diferencial/7191184/
S3 | MPXV5010DP | Ventilator:1351-01 | https://es.rs-online.com/web/p/circuitos-integrados-de-sensor-de-presion-diferencial/7191184/
S4 | MPXV5004DP | Ventilator:1351-01 | https://es.rs-online.com/web/p/sensores-de-presion/9227399/
S5 | MPVZ5010GW7U | Ventilator:1560-03
S6 | MPVZ5010GW7U | Ventilator:1560-03
SW1 | MUTE | Button_Switch_THT:SW_PUSH_6mm_H13mm | ~
SW2 | HIST | Button_Switch_THT:SW_PUSH_6mm_H13mm | ~
SW3 | VOL_MIN | Button_Switch_THT:SW_PUSH_6mm_H13mm | ~
SW4 | VOL | Button_Switch_THT:SW_PUSH_6mm_H13mm | ~
SW5 | BPM | Button_Switch_THT:SW_PUSH_6mm_H13mm | ~
SW6 | IP | Button_Switch_THT:SW_PUSH_6mm_H13mm | ~
SW7 | - | Button_Switch_THT:SW_PUSH_6mm_H13mm | ~
SW8 | VOL_MAX | Button_Switch_THT:SW_PUSH_6mm_H13mm | ~
SW9 | PMAX | Button_Switch_THT:SW_PUSH_6mm_H13mm | ~
SW10 | BREATH | Button_Switch_THT:SW_PUSH_6mm_H13mm | ~
SW11 | EP | Button_Switch_THT:SW_PUSH_6mm_H13mm | ~
SW12 | + | Button_Switch_THT:SW_PUSH_6mm_H13mm | ~
SW13 | RESET_M | Button_Switch_THT:SW_PUSH_6mm_H13mm | ~
SW14 | RESET_C | Button_Switch_THT:SW_PUSH_6mm_H13mm | ~
U1 | LM358 | Package_SO:SOIC-8-1EP_3.9x4.9mm_P1.27mm_EP2.41x3.3mm | https://es.rs-online.com/web/p/amplificadores-operacionales/1787509/
U2 | LM78M05_TO252 | Package_TO_SOT_SMD:TO-252-2 | https://es.rs-online.com/web/p/reguladores-de-tension-lineal/8578558/
U3 | PIC18F46K42 | Ventilator:QFN-40-1EP_5x5mm_P0.4mm_EP3.6x3.6mm_MedThermalVias
U4 | LM78M05_TO252 | Package_TO_SOT_SMD:TO-252-2 | https://es.rs-online.com/web/p/reguladores-de-tension-lineal/8578558/
U5 | PIC18F46K42 | Ventilator:QFN-40-1EP_5x5mm_P0.4mm_EP3.6x3.6mm_MedThermalVias
U6 | LCD | Ventilator:LCD_2x16 | https://es.rs-online.com/web/p/displays-monocromos-lcd/1631922/
U7 | LCD | Ventilator:LCD_2x16 | https://es.rs-online.com/web/p/displays-monocromos-lcd/1631922/

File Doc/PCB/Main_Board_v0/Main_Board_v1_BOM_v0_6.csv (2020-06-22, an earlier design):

Reference | Quantity | Value | Footprint | Datasheet
C10 C2 C6 C3 C4 C20 C22 C24 C23 C25 C18 C27 C26 | 13 | 1uF | Capacitor_THT:C_Rect_L13.0mm_W4.0mm_P10.00mm_FKS3_FKP3_MKS4 | https://es.rs-online.com/web/p/condensadores-de-pelicula-de-poliester/1710733/~
C12 C13 C11 C8 C9 C1 C7 C21 C19 C14 C16 C29 C17 C28 C30 | 15 | 100nF - 100V | Capacitor_THT:C_Rect_L7.2mm_W2.5mm_P5.00mm_FKS2_FKP2_MKS2_MKP2 | https://es.rs-online.com/web/p/condensadores-de-pelicula-de-poliester/1710743/
C5 C15 | 2 | 4.7uF 50V | Capacitor_THT:CP_Radial_D5.0mm_P2.00mm | https://es.rs-online.com/web/p/condensadores-de-aluminio/1701286/
D1 D4 D2 D3 | 4 | 1N4007 | Diode_THT:D_DO-41_SOD81_P10.16mm_Horizontal | https://es.rs-online.com/web/p/diodos-schottky-y-rectificadores/6491187/
J10 | 1 | BPM | Ventilator:PushButton | https://es.rs-online.com/web/p/botones-pulsadores/7346827/
J11 | 1 | UART | Connector_PinHeader_2.54mm:PinHeader_1x03_P2.54mm_Vertical | ~
J12 | 1 | I2C Interface LCD_C | Ventilator:PH_4_pol | ~
J13 | 1 | BUZZER_C | Connector_PinHeader_2.54mm:PinHeader_1x02_P2.54mm_Vertical | https://es.rs-online.com/web/p/componentes-de-piezo-buzzer/6173097/?searchHistory=%7B%22enabled%22%3Atrue%7D
J14 | 1 | MUTE | Ventilator:PushButton_LED | https://es.rs-online.com/web/p/botones-pulsadores/8207521/
J15 | 1 | HISTORY | Ventilator:PushButton | https://es.rs-online.com/web/p/botones-pulsadores/7346827/
J16 | 1 | IP | Ventilator:PushButton | https://es.rs-online.com/web/p/botones-pulsadores/7346827/
J17 | 1 | - | Ventilator:PushButton | https://es.rs-online.com/web/p/botones-pulsadores/7346827/
J18 | 1 | BREATH | Ventilator:PushButton_LED | https://es.rs-online.com/web/p/botones-pulsadores/8207533/
J19 | 1 | EP | Ventilator:PushButton | https://es.rs-online.com/web/p/botones-pulsadores/7346827/
J2 J1 J7 | 3 | TE_3.5mm_Screwless_P2 | Ventilator:PinHeader_1x02_Screwless_3.5mm | https://es.rs-online.com/web/p/bloques-terminales-para-pcb/1232052/
J20 | 1 | + | Ventilator:PushButton | https://es.rs-online.com/web/p/botones-pulsadores/7346827/
J21 | 1 | VOL_MIN | Ventilator:PushButton | https://es.rs-online.com/web/p/botones-pulsadores/7346827/
J22 | 1 | VOL | Ventilator:PushButton | https://es.rs-online.com/web/p/botones-pulsadores/7346827/
J23 | 1 | VOL_MAX | Ventilator:PushButton | https://es.rs-online.com/web/p/botones-pulsadores/7346827/
J3 | 1 | UART_M | Connector_PinHeader_2.54mm:PinHeader_1x03_P2.54mm_Vertical | ~
J4 J24 | 2 | Conn_01x08 | Connector_PinHeader_2.54mm:PinHeader_1x08_P2.54mm_Horizontal | ~
J5 | 1 | BUZZER | Ventilator:PH_2_pol | https://es.rs-online.com/web/p/componentes-de-piezo-buzzer/6173097/?searchHistory=%7B%22enabled%22%3Atrue%7D
J6 | 1 | I2C Interface LCD_M | Ventilator:PH_4_pol | ~
J8 | 1 | SV2 | Ventilator:PinHeader_1x02_Screwless_3.5mm | https://es.rs-online.com/web/p/bloques-terminales-para-pcb/1232052/
J9 | 1 | SV3 | Ventilator:PinHeader_1x02_Screwless_3.5mm | https://es.rs-online.com/web/p/bloques-terminales-para-pcb/1232052/
MK1 | 1 | Microphone | Ventilator:MIC | https://es.rs-online.com/web/p/componentes-de-microfono-para-condensador/7243125/?searchHistory=%7B%22enabled%22%3Atrue%7D
Q1 Q2 Q3 | 3 | STP24NF10 | Package_TO_SOT_THT:TO-220-3_Vertical | https://es.rs-online.com/web/p/mosfet/6875377/
R24 | 1 | 22k | Resistor_THT:R_Axial_DIN0207_L6.3mm_D2.5mm_P10.16mm_Horizontal | ~
R3 R5 | 2 | 220k | Resistor_THT:R_Axial_DIN0207_L6.3mm_D2.5mm_P10.16mm_Horizontal | ~
R4 R2 R11 R9 R25 R35 R19 R20 R21 R22 R23 R18 R27 R28 R31 R32 R30 R36 | 18 | 10k | Resistor_THT:R_Axial_DIN0207_L6.3mm_D2.5mm_P10.16mm_Horizontal | ~
R6 R14 R26 | 3 | 50 | Resistor_THT:R_Axial_DIN0207_L6.3mm_D2.5mm_P10.16mm_Horizontal | ~
R7 R10 R8 R12 R1 R34 R33 R16 R17 R15 R13 R29 | 12 | 470 | Resistor_THT:R_Axial_DIN0207_L6.3mm_D2.5mm_P10.16mm_Horizontal | ~
S1 S2 S3 S4 | 4 | MPXV5004DP | Ventilator:1351-01 | https://es.rs-online.com/web/p/sensores-de-presion/9227399/
TP3 TP2 TP1 TP4 TP7 TP6 TP5 TP8 TP12 TP11 TP10 TP13 | 12 | TestPoint | Ventilator:LCD_DRILL | ~
TP9 | 1 | TestPoint_Alt | Ventilator:pcb | ~
U1 | 1 | LM358 | Package_DIP:DIP-8_W7.62mm_LongPads | http://www.ti.com/lit/ds/symlink/lm2904-n.pdf
U2 U4 | 2 | LM7805_TO220 | Package_TO_SOT_THT:TO-220-3_Vertical | http://www.fairchildsemi.com/ds/LM/LM7805.pdf
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

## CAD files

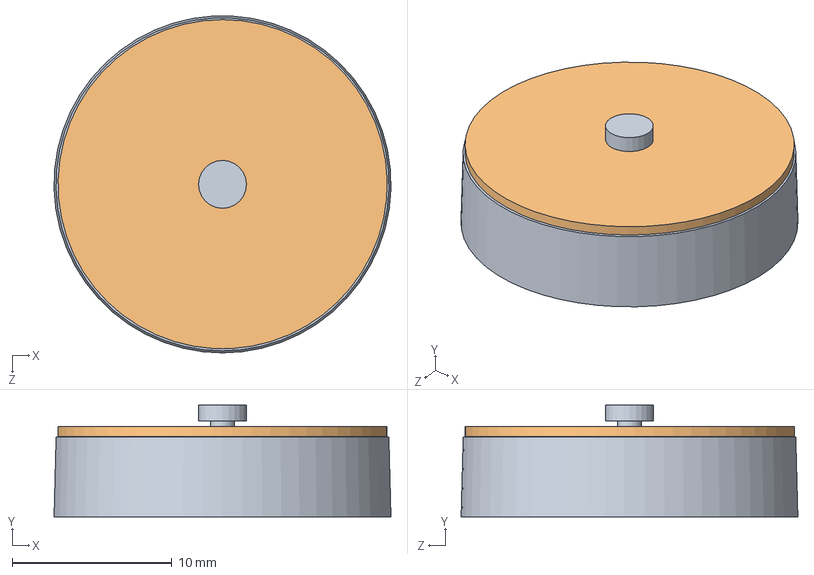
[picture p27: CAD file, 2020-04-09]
Doc/Ideas/flow_sensor_port-1/nr_valve.SLDASM
21.1 x 7.00 x 21.1 mm
nr_frame
nr_diaphragm

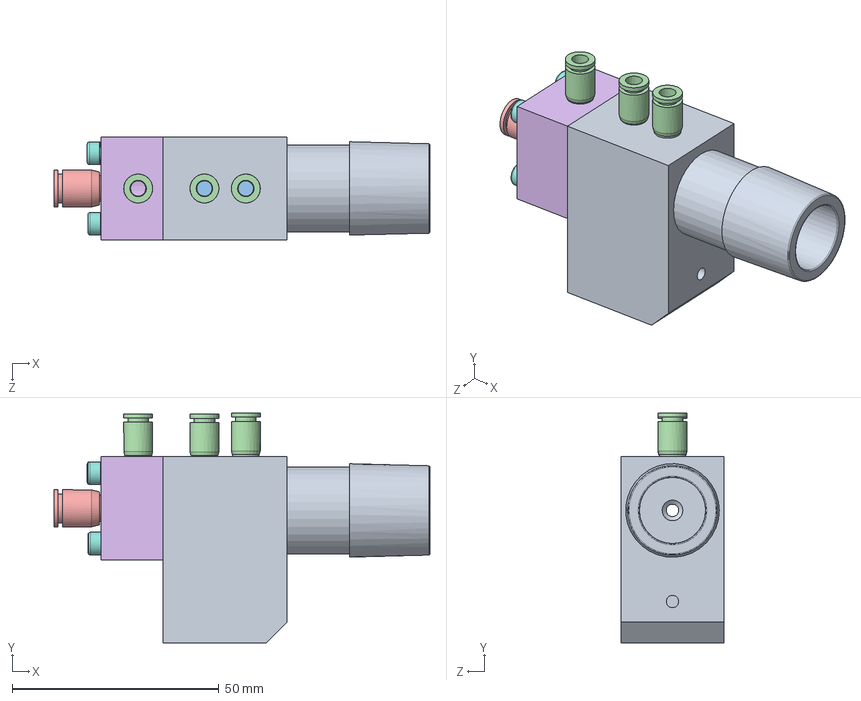
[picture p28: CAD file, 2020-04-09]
Doc/Ideas/flow_sensor_port-1/fresh_gas_port.SLDASM
90.8 x 55.5 x 25.0 mm
block
nr_frame
nr_diaphragm
4mm hose connector x 3
6mm hose connector
fs_block
o-ring_lrg
bolt_M3 x 4

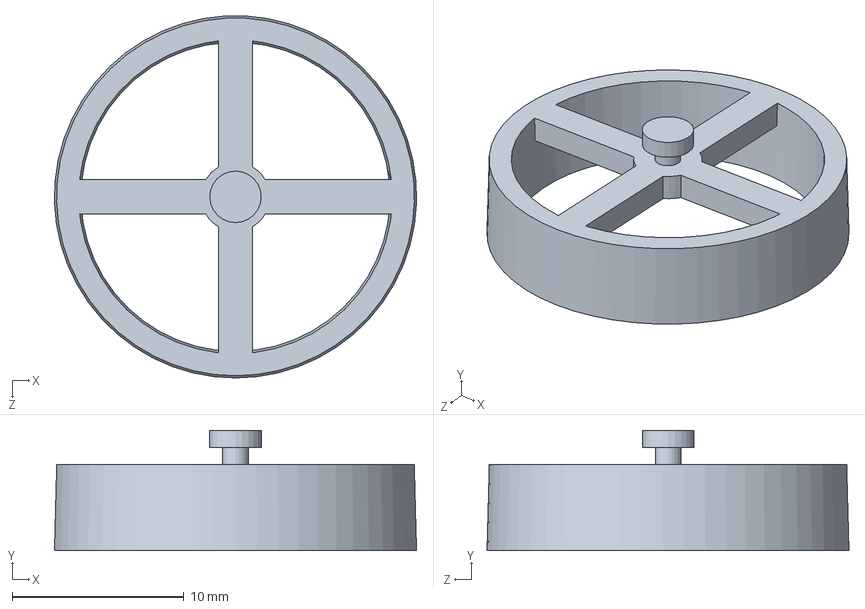
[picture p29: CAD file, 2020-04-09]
Doc/Ideas/flow_sensor_port-1/nr_frame.SLDPRT
21.1 x 7.00 x 21.1 mm

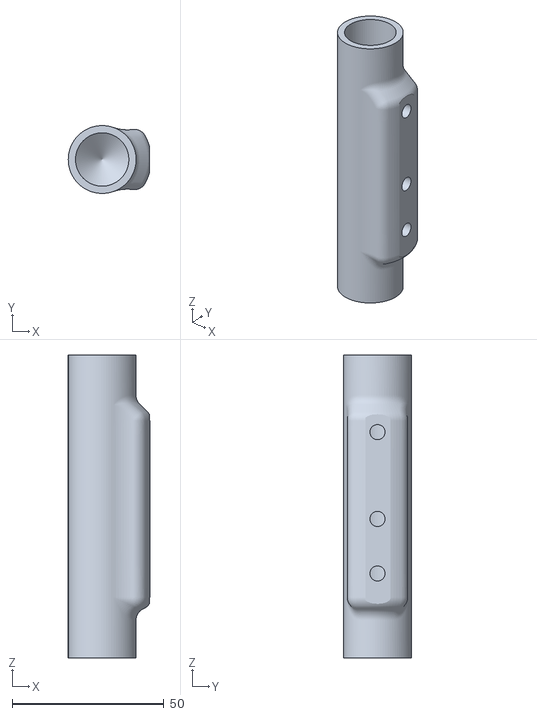
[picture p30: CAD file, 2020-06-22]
Doc/Mech/FlowSensor.stl
26.9 x 22.4 x 100.0

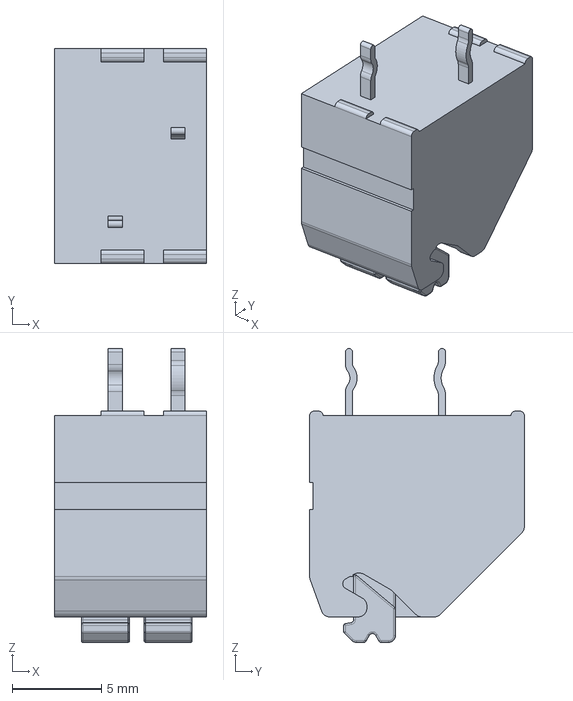
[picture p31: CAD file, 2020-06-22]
Doc/PCB/Main_Board_v1_3_SMD/c-1-2834011-2-2-3d.stp
8.50 x 12.0 x 16.4 mm

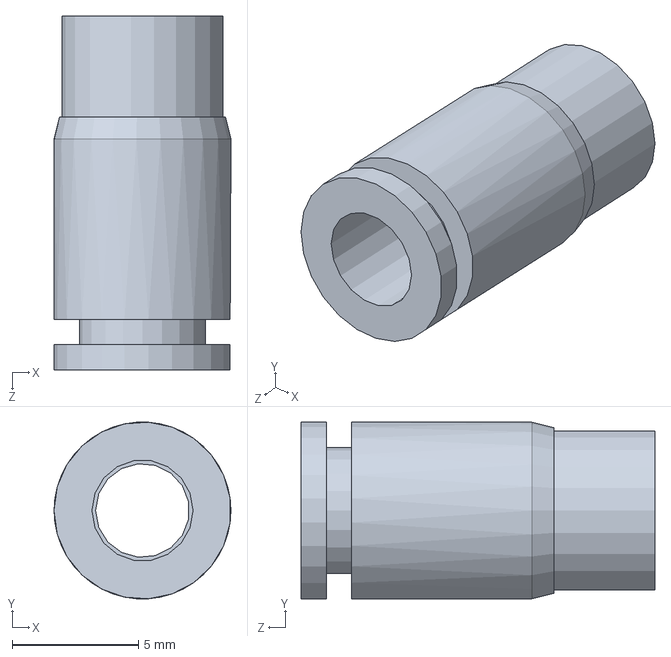
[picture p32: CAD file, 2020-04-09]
Doc/Ideas/flow_sensor_port-1/4mm hose connector.SLDPRT
7.00 x 6.98 x 14.0 mm

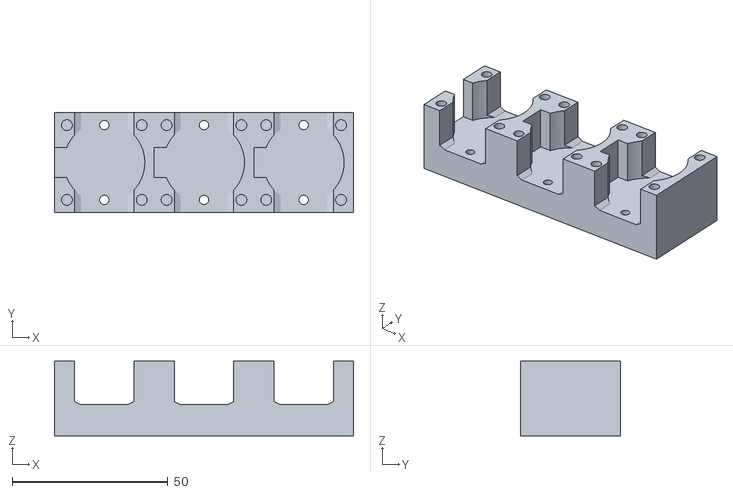
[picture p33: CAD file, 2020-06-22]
Doc/Mech/ValvHolderVert.stl
96.0 x 32.0 x 24.0

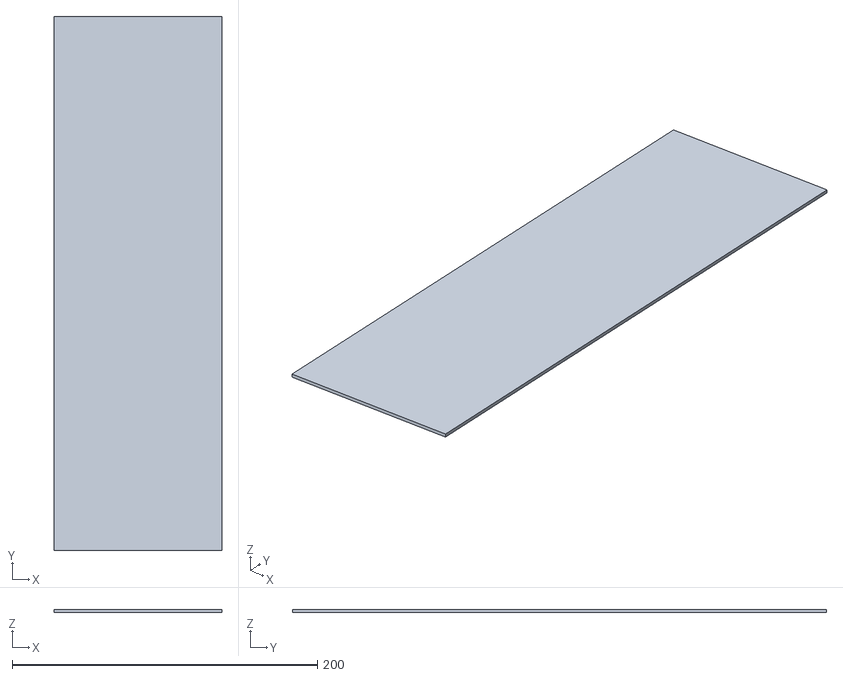
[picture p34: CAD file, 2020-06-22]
Doc/PCB/Main_Board_v1_2/panel_empty.stl
110.0 x 350.0 x 2.00

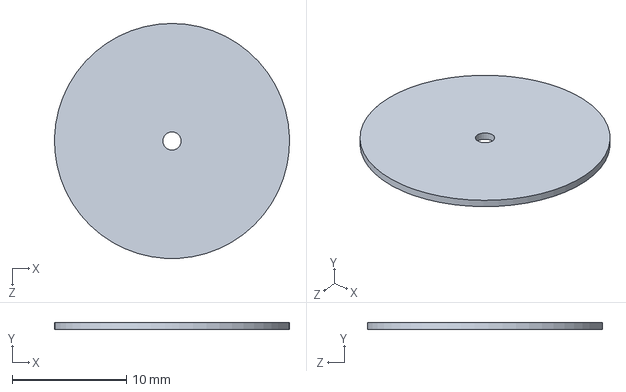
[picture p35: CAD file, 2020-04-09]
Doc/Ideas/flow_sensor_port-1/nr_diaphragm.SLDPRT
20.6 x 0.6 x 20.6 mm

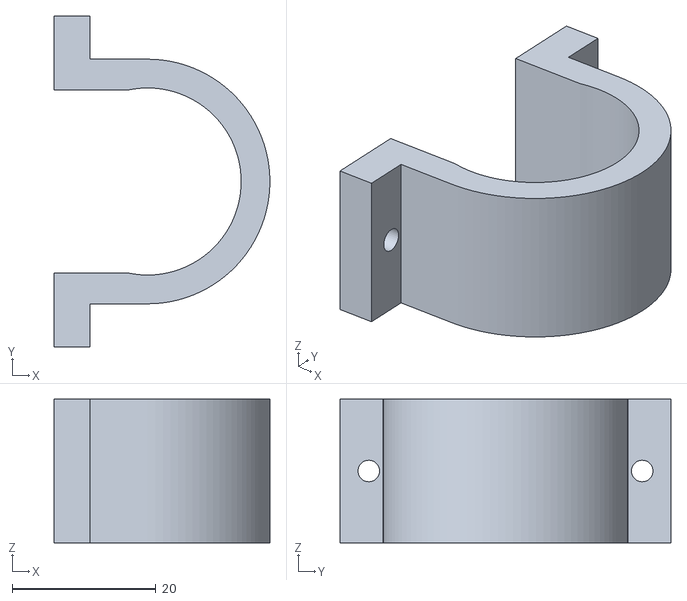
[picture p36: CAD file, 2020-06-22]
Doc/Mech/TubeHolderShort.stl
30.0 x 46.0 x 20.0

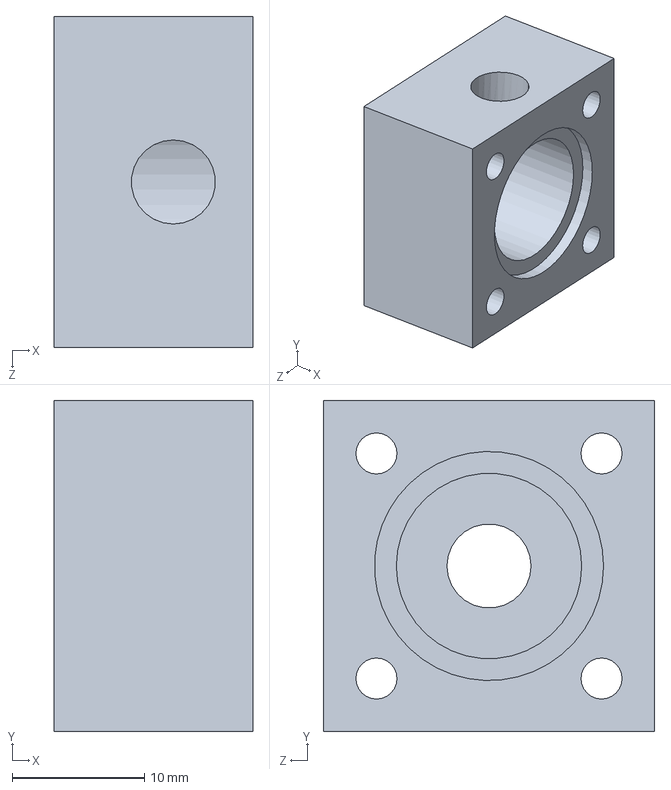
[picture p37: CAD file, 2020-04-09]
Doc/Ideas/flow_sensor_port-1/fs_block.SLDPRT
15.0 x 25.0 x 25.0 mm

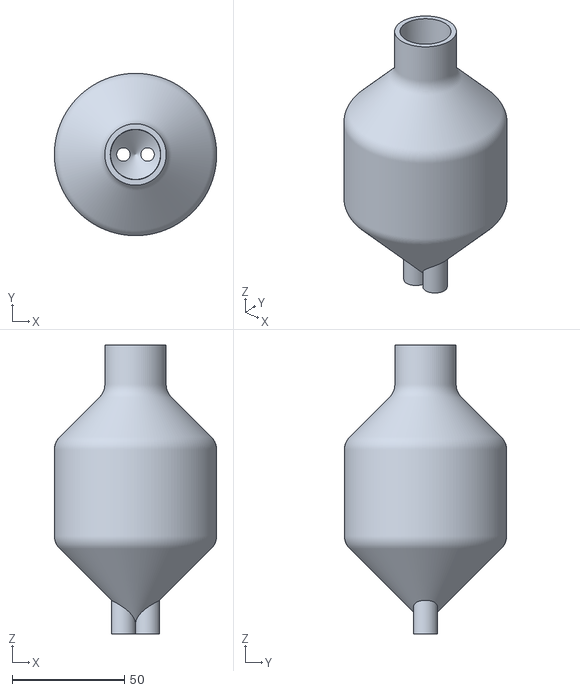
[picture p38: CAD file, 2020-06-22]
Doc/Mech/Dampener_dual.stl
72.4 x 72.4 x 128.9

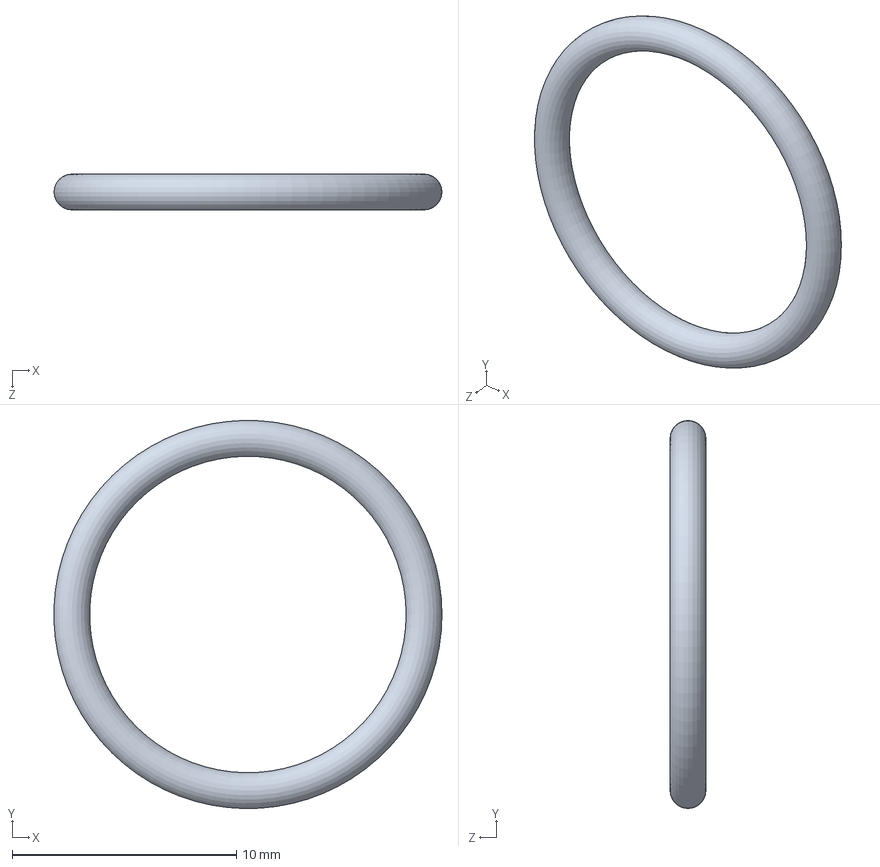
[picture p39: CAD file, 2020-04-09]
Doc/Ideas/flow_sensor_port-1/o-ring_lrg.SLDPRT
17.3 x 17.3 x 1.60 mm

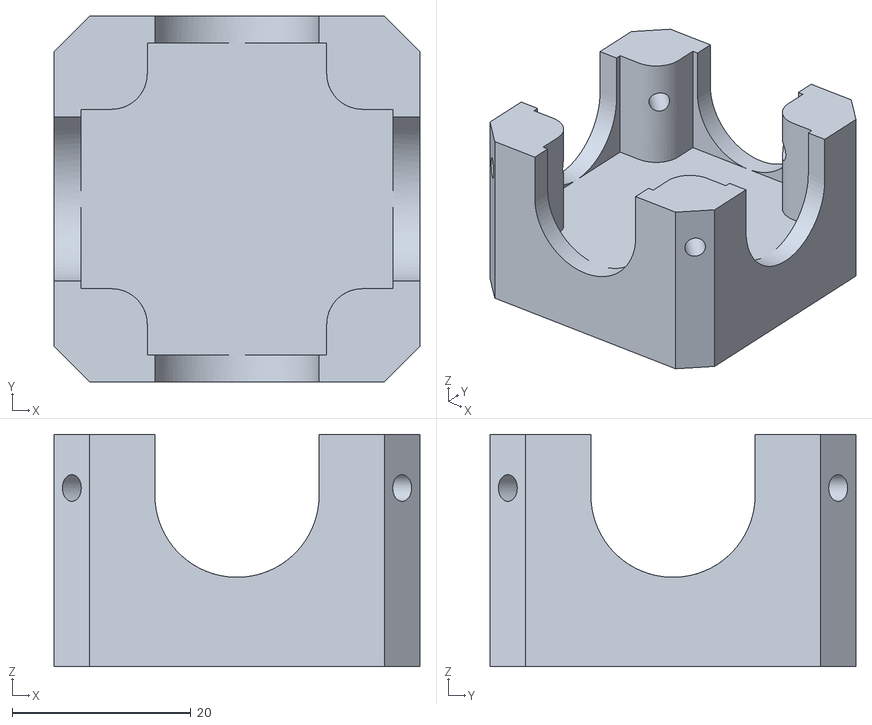
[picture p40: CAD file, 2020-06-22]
Doc/Mech/PresRegHolder.stl
41.0 x 41.0 x 26.0

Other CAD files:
Doc/caratula.FCStd
Doc/PCB/Main_Board_v1_2/Panel&Board.FCStd
Doc/Mech/flowsensor_6mm.stl
Doc/Mech/ValvHolderVertSingle.stl
Doc/Ideas/flow_sensor_port-1/6mm hose connector.SLDPRT
Doc/Ideas/flow_sensor_port-1/block.SLDDRW
Doc/Ideas/flow_sensor_port-1/block.SLDPRT
Doc/Ideas/flow_sensor_port-1/bolt_M3.SLDPRT
Doc/Ideas/flow_sensor_port-1/directional_valve.SLDDRW
Doc/Ideas/flow_sensor_port-1/flow_sensor_block.SLDDRW
Doc/Mech/Adapter22m_dual.stl
Doc/Mech/BatterySupport.stl
Doc/Mech/TubeHolderTall.stl
Doc/PCB/Main_Board_v0/pcb.dwg
Doc/PCB/Main_Board_v0/pcb.dxf
Doc/PCB/Main_Board_v1/Pannel.FCStd
Doc/PCB/Main_Board_v1/pcb.dwg
Doc/PCB/Main_Board_v1/pcb.dxf
Doc/PCB/Main_Board_v1_1/Panel&Board.FCStd

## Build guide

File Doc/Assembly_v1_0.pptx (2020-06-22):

## Airvita

Assembly guide

## Airvita

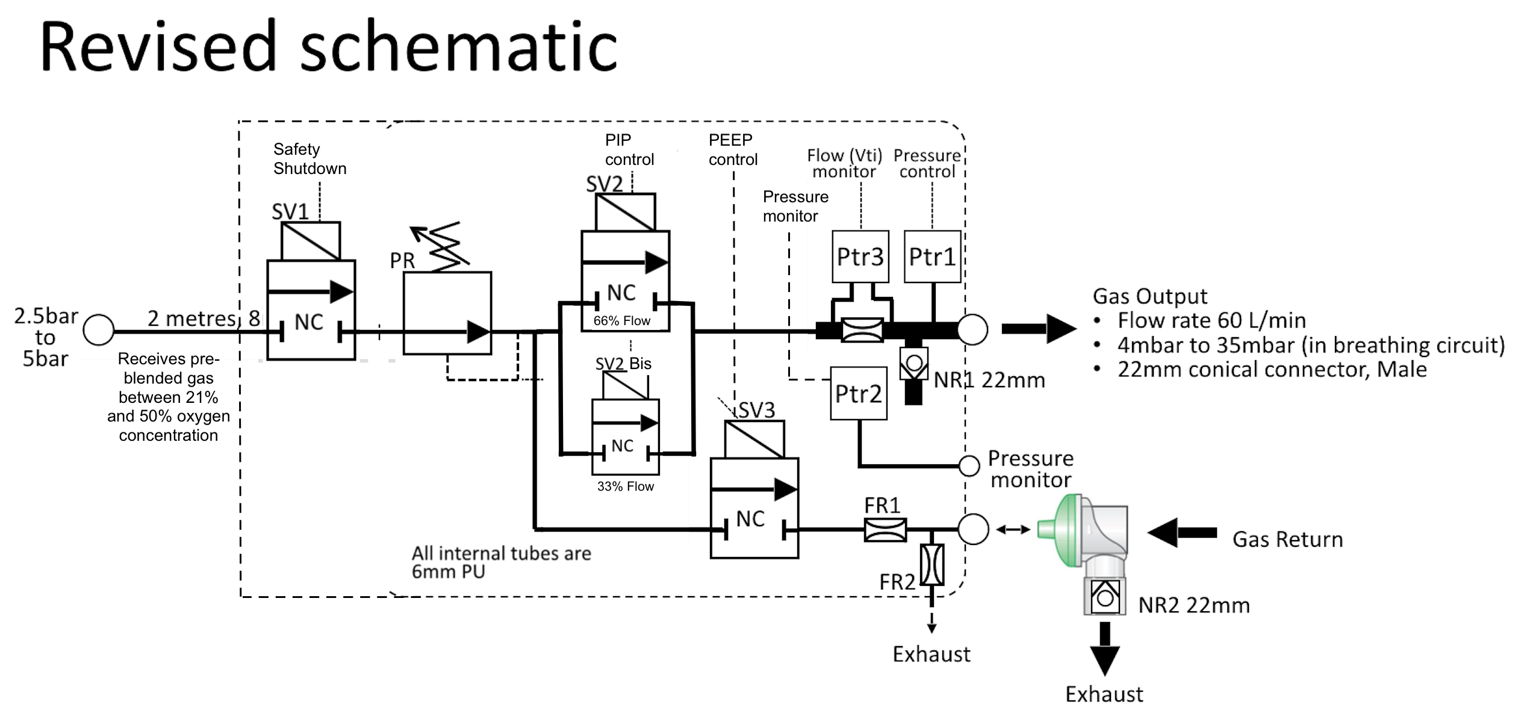
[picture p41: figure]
Imagen

Ptr4

## Airvita assembly

- Input stage

8mm

12V Battery

+

SV1

PR

6mm

6mm

SV2
High flow

SV2-bis
SV4
Low flow

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
## Airvita assembly

- Output stage

8mm

12V Battery

+

SV1

PR

6mm

6mm

SV2
High flow

SV2-bis
SV4
Low flow

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
## Airvita assembly

- Sensing part

8mm

12V Battery

+

SV1

PR

6mm

6mm

SV2
High flow

SV2-bis
SV4
Low flow

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
## Airvita assembly

- Sensing part

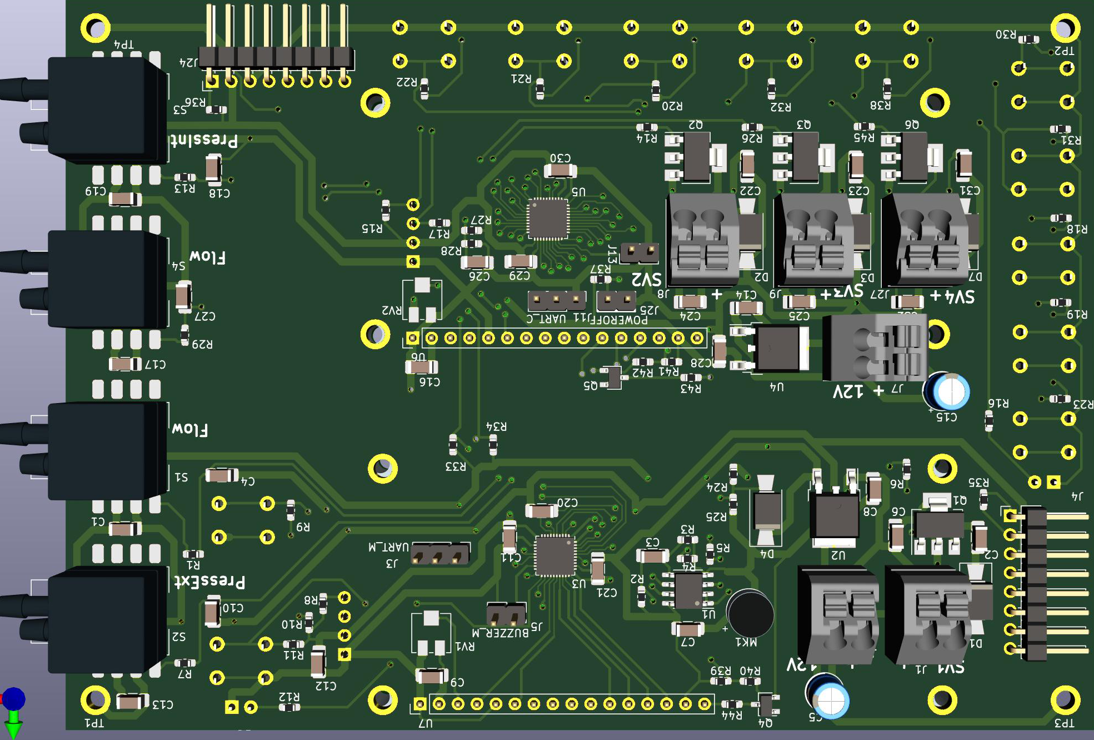
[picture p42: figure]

## Airvita assembly

- Cabling - Power supply

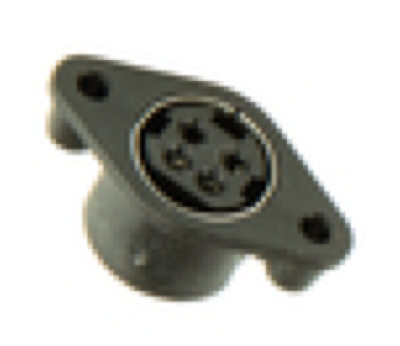
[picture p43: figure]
Imagen
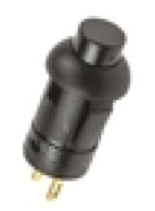
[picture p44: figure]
Imagen

12V Battery

+

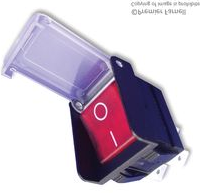
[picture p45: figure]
Imagen

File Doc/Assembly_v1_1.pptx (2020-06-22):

## Airvita

Assembly guide

## Airvita

Imagen

Ptr4

FR3

## Airvita assembly

- Input stage

8mm

12V Battery

+

SV1

PR

6mm

6mm

SV2
High flow

SV2-bis
SV4
Low flow

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
## Airvita assembly

- Output stage

8mm

12V Battery

+

SV1

PR

6mm

6mm

SV2
High flow

SV2-bis
SV4
Low flow

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
## Airvita assembly

- Sensing part

8mm

12V Battery

+

SV1

PR

6mm

6mm

SV2
High flow

SV2-bis
SV4
Low flow

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
## Airvita assembly

- Sensing part


## Airvita assembly

- Cabling - Power supply

Imagen
Imagen

12V Battery

+

Imagen

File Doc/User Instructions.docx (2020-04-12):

Ventilator 2020

User Guide

V 1.0

5 April 2020

Model: Ventilator 2020

Manufacturer: Name and address of the organisation releasing the device into the market under their name

Table of Contents

# 1 Introduction

## Intended use

The ventilator is intended for providing mass intensive respiratory care, in facilities that might be lacking in full hospital infrastructure and clinical experiences – such as under pandemic emergency conditions.

The device is intended for use with adult and young adult patients from 50kg and upwards.

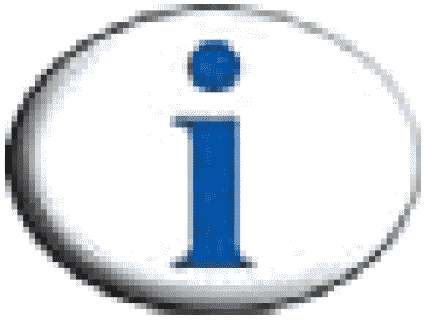
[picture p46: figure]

- Ventilator requires a pre-blended air-oxygen mixture.
- Ventilation efficiency should be monitored using a TcCO2 or EtCO2 device, to measure CO2 elimination; and a SpO2 device, to measure blood oxygen saturation.
- Other vital signs monitoring is also recommended.

## Device

The ventilator is designed for a simplified clinical protocol that demands minimal training and re-training. It is further designed to be mass-producible and requiring minimal maintenance. The gas cycling operation is designed to minimise oxygen consumption.

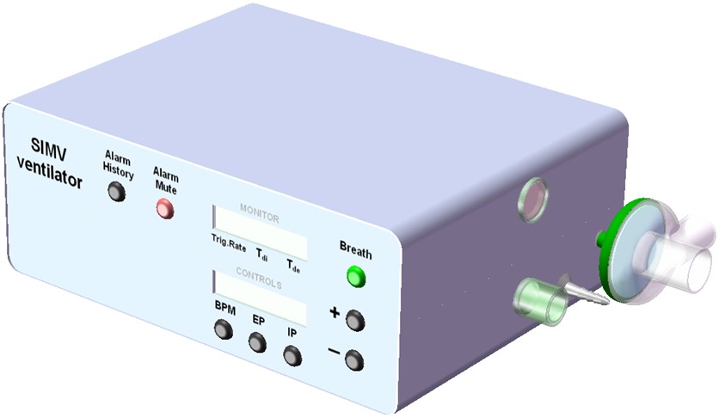
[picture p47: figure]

The ventilator uses conventional Pressure Controlled SIMV (Synchronised Intermittent Mandatory Ventilation) mode of ventilation only. It interfaces with intubated, unconscious and semi-conscious, patients; and it interfaces with pressure ventilation masks on conscious patients. There is no need to select and switch between alternative modes or interfaces.

For purpose of simplicity, the I:E ratio (Inspiratory-Expiratory) is fixed 1:2. Inspiration flow rate fixed 60L/min, which produces an IP rise time of about 0.45s into a 600mL lung.

SIMV behaves as PSV (Pressure Support Ventilation) when the patient makes full efforts, and it behaves as CMV (Continuous Mandatory Ventilation) if the patient does not make any efforts. When used with a mask on a conscious, spontaneously breathing patient, the SIMV behaves as nPSV or Synchronised BiPAP (by setting IP low). Switching the IP cycle off (or setting it equal to PEEP) makes SIMV behaves as CPAP (whether the patient is intubated or has a mask interface).

The device is not intended to be marketed as a commercial medical device. The device conforms to medical device requirements for basic safety and essential performance. There is not, yet, any basis for proving the clinical efficacy of the device.

The ventilator is designed to operate in combination with an external power supply, a breathing circuit and a respiratory gas humidifier (HME or water chamber).

The ventilator features two one-way valves, which enables the spontaneously breathing patient to take in fresh ambient air in case of power and gas supply failures.

## Combination devices

The ventilator receives electrical power from an external power supply. Under the definitions for medical electrical equipment (standard IEC 60601-1), the ventilators forms part of a mains power connected Medical Electrical System (MES). The ventilator itself is not a mains connected Medical Electrical Equipment (MEE). The power supply unit must therefore conform to national standards for MEE (e.g. it should have CE or national equivalent mark). The power cord must be attached to the ventilator, using a P-clip, to prevent accidental disconnection.

The 22mm breathing circuit should also meet medical device standards. The simplest configuration of breathing circuit is preferred. The circuit must as minimum contain an HME (Heat Moisture Exchange) device. The breathing circuit must have a maximum compliance of 5ml/mbar (or 5ml/cmH2O) and a maximum resistance of 1mbar (or 1 cmH2O) at 30L/min flow rate. These values are met by most available 22mm circuits in the market.

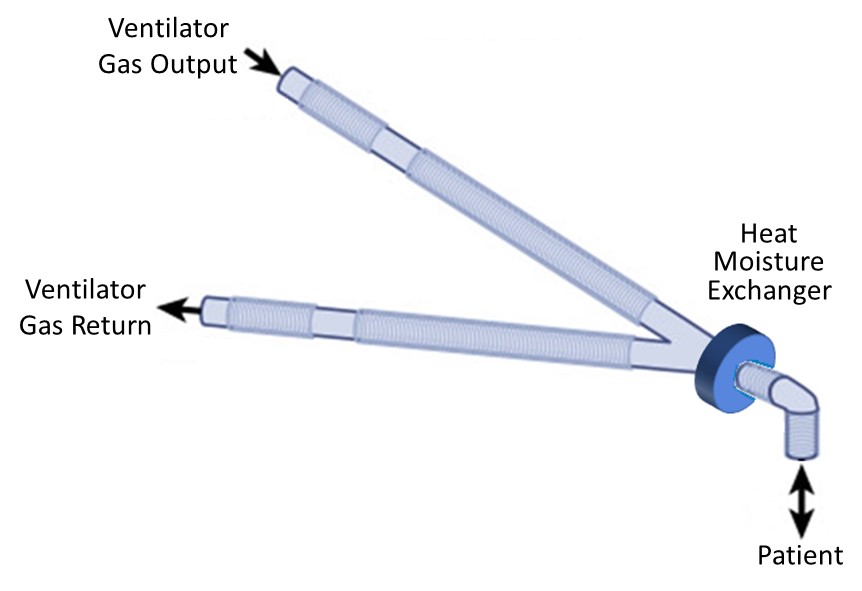
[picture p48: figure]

The HME may be replaced by introducing a water bath or ultrasonic humidifier on the ‘Gas Output’ side of the breathing circuit. This should normally be matched by a water trap on the ‘Gas Return’ side of the circuit, to collect the moisture that otherwise collects inside the tubes.

In the event of total power or gas supply failure, the ventilator incorporates a pair of low resistance directional valves to enable spontaneous breathing, without rebreathing. The resistance to breathing depends on the breathing circuit and any attachments (e.g. bacteria filter).

The ventilator may use a combination ultrasonic nebulizer, which does not add an extra gas flow to the breathing circuit. DO NOT use gas driven nebulizers.

Exhalation exhaust port is standard 22mm connector, enabling bacterial filter or (via adapter) gas scavenging to reduce the risk of cross-contamination

At system level, the ventilator forms part of a scalable multi-devices arrangement. The ventilators receive pre-blended gas, from one of selectable supply lines. This arrangement significantly simplifies the ventilator design. The example here shows 2 parallel gas lines (but this could be 3 or 4), supplying pre-blended 25% and 40% FiO2 (finally inspired oxygen concentration) respectively. The FiO2 settings can be changed to whatever clinicians prescribe for the particular group of ventilators.

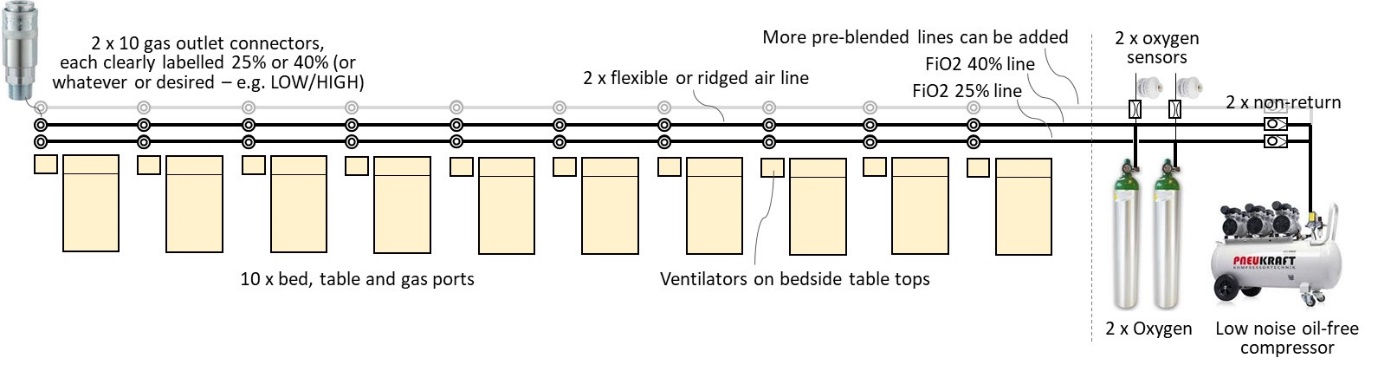
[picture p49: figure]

## User responsibility

The ventilator and the accessories for it are designed for use in accordance with the displayed labels and supplied instructions. User must be suitably, clinically trained and authorised by their clinical management to operate the ventilator. Oxygen is a drug and should be prescribed as such.

The equipment and gas supply hoses must be periodically checked, maintained and components repaired and replaced, when necessary, for the equipment to operate safely and reliably.

Parts that have failed, in whole or in part, or exhibit excessive wear, or are contaminated, or are otherwise at the end of their useful life, should not be used and must be replaced immediately with approved parts.

The use of oxygen requires special precaution to avoid fire hazards. Keep all sources of ignition away when oxygen is in use. Do not use oil or grease on high-pressure oxygen fittings.

## Warnings

### DO NOT use a gas flow driven Nebulizer during ventilation.

### A hazard can exist when equipment with similarly sounding audible alarms are used in the same area. Observe the alarm lights as well as listening.

### An alternative form of ventilation should be on standby.

### Use a power supply unit that is conformity assessed to national standards for Medical Electrical Equipment (e.g. has a CE or national equivalent mark).

### The ventilator must be connected to a suitably rated and grounded electrical power source, via the power supply unit.

### The ventilator IS NOT compatible with MRI scanner control zones and other equipment radiating high electro-magnetic power.

### In case of low confidence in the contamination status of the supply gas, then use a particle and appropriate filer on the ‘Gas Output’ port.

### If the battery is allowed to completely discharge, then it should be recharged a soon as possible. This is to avoid damaging the battery by allowing it to remain in a deep discharged state.

### If the ventilator is not going to be used for a period in excess of 40 days then disconnect the battery from the power supply.

### Failure to comply with the recommended service and maintenance programs could lead to injury of the patient, operator or damage to the ventilator.

## Clinical warnings

### Use conventional Pressure Control SIMV ventilation only.

### Patient breath triggering is limited to one trigger sensitivity with strong spontaneous efforts.

### There are inherent risks in the use of mechanical ventilation. Use appropriate monitoring of patient status and outcomes.

### Failure to take corrective action when the alarms are activated could result in serious injury to a patient.

# 2 User interface

User interface is divided into a ‘Monitor’ and a ‘Control’ section.

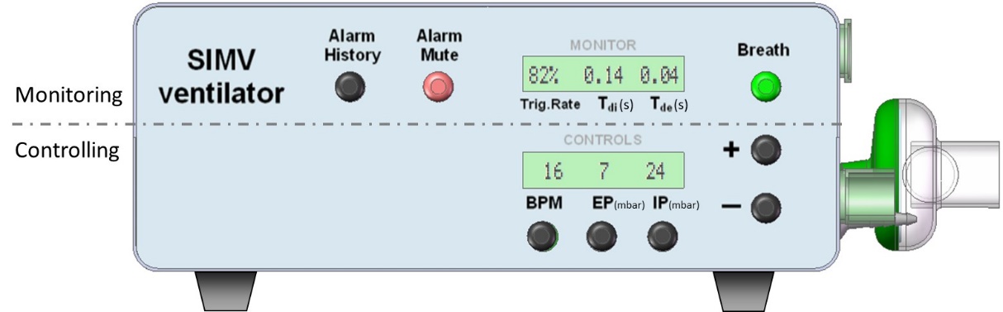
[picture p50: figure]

The ventilator monitors and displays 3 values:

- Trigger Rate: The percentage of delivered breaths instigated by spontaneous patient effort. Its trend indicates patient progress or deterioration.
- Tdi: IP rise time, indicates lung compliance, but also if gas supply becomes restricted.
- Tde: Expiration wave decay time, indicates if the bacterial filter or patient circuit is soiled (excessively resistive) and need replacing. Where a small resistance is added to the exhaust (e.g. bacteria filter) the Tde can also help indicate lung obstruction (fluids, secretions).

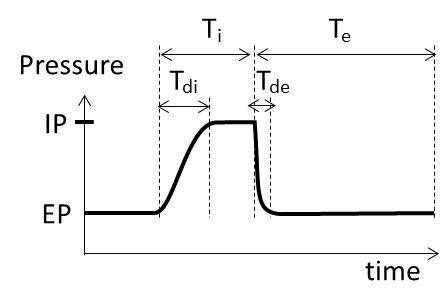
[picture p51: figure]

The ‘Alarm’ button lights up or flashes when an alarm condition exists. Alarm messages appear in the monitor display (temporarily flashing the values).

The ‘Breath’ button lights up during the IP phase, to indicate ventilator cycling.

The ventilator has 4 controls:

- BPM (Breath Per Minute): 10 to 30, in 1 steps.
- EP (Expiration Pressure, same as PEEP): 4 to 25mbar, in 1 steps.
- IP – Inspiration Pressure (same as PIP): 4 to 35mbar, in 1 steps.
- Manual breath: Active while ‘Breath’ button is pressed.

Note: 1 mbar = 1.02 cmH2O and the 2 units can be considered practically equal.

## Control

To power up the ventilator, press the ‘ON/OFF’ switch on the rear. Observe the power-up self-test correctly displays LEDs and the display digits.

To power down the ventilator, press the ‘ON/OFF’ switch on the rear. The monitor will display a message for 5 seconds saying ‘Power OFF?’. During this short period, press and hold any of the facia buttons for 2 seconds. If the 5-second message is missed, then simply flick the ‘ON/OFF’ switch again, to restart the 5-second message.

If none of the buttons are held for 2 seconds, or just pressed momentarily, the message will disappear and the ventilator will continue to operate under battery power. This enables moving the patient or intra-hospital transport.

Adjusting a control parament:

1. Press the button underneath the parameter to be adjusted.
2. Observe that the parameters value starts flashing. It will time out after 5 seconds of inactivity.
3. Adjust the flashing parameter value using the +/- buttons.
4. Press parameter control button again to confirm the new setting.

The ‘Breath’ button delivers a manual breath. This is used to re-recruit the lung following a procedure that temporarily disconnected the patient from the ventilator, such as during suctioning or while changing the FiO2 level.

The ‘Alarm Mute’ button will suspend the alarm sounder for 120 seconds. It will also un-latch any existing alarm (see section 3.2). Alarms will trigger or re-trigger while the sound is muted. Observe the message display.

The ‘Alarm History’ cycles through the last 10 alarm messages.

## Setting up the ventilator breathing circuit

Before switching on the ventilator (to avoid unnecessary alarming):

- Push the exhalation valve onto the ventilator’s spigot labelled ‘Gas Return’.
- Push the exhalation valve’s pressure tube to the ventilator’s spigot labelled ‘Patient Pressure’
- Connect the circuit expiratory limb to the exhalation valve’s 22mm Female on the ventilator’s ‘Gas Return’ port.
- Connect the circuit inspiratory limb to the ventilator’s 22mm Male ‘Gas Output’ port.
- Connect the HME (or alternative humidification).
- Switch on the ventilator and verify for leaks/poor connections.

The circuit may be set up in advanced and verified using a test lung; and then capped off to protect hygiene.

## Monitoring

Periodically observe and record the 3 monitored values. Look for trends that could indicate a change in patient condition, lung function or ventilator system performance.

- TcCO2 or EtCO2, and SpO2, which indicates the blood gasses, should also be recorded (EtCO2 tends to represent the blood CO2).
- It is recommended to record the trending of other vital signs.
- Any changes in the trends should be reviewed or investigated by a suitably qualified clinician, with view to prescribe adjustments to the ventilator settings or associated therapy.

A decreasing Trigger Rate could indicate a deterioration in patient conditions.

A decreasing Tdi could indicate declining lung compliance and onset of ARDS (Acute Respiratory Distress Syndrome). The clinician might want to review (with blood gas measures) and consider whether to increase IP to achieve sufficient Tidal Volume, or increase BPM to achieve sufficient Minute Volume.

An increasing Tdi could indicate improving lung compliance. The clinician might want to review (with blood gas measures) and consider if IP can be reduced, to maintain a steady Tidal Volume and prevent over-distending the lung.

An increasing Tdi, if it happens across all patients connected to the same gas supply, could also indicate that gas supplies are ‘starved’.

An increasing Tde could indicate increasing resistance in the breathing circuit exhalation path, as result of tubing or bacterial filer being soiled.

# 3 Display messages and alarms

## Messages

The user interface messages displayed on the two 16 character wide LCDs.

User message | Description | Action
Monitor and control parameter values | Normal operation, within expected tolerances. | None
Audio Paused (message alternates with underlying original message) | Indicates that user has activated the alarm audio cancel or alarm ‘pre-mute’. | Pauses alarm audio for 120 seconds, or until button or is pressed again. Un-latches any latched alarm conditions.
Confirm Change | User has commenced adjustment of a BPM, EP or IP parameter. | Adjustment is NOT accepted until parameter button is pressed again. Times out and reverts to prior values after 5 sec of inaction.
Ventilator v1.0 | Version display during power-on-self-test. | Clears itself on completion of the power-on-self-test.
Ready... | Indicates that power-on-self-test has completed. | Clears itself after 2 sec
<no message> | Indicates that a particular history log location does not have any stored event (i.e. alarm has not occurred) | None
Power OFF??? | The user has moved the rear mechanical power switch to OFF position. | Press and hold any button on the facia for 2 sec. To power down. OR, do nothing, to continue to operate in battery power mode.

## Alarm messages

Alarm messages ranked in order of priority. The current message of highest priority ranking is stored in the history log. Simultaneous lower ranking messages are often the consequence of a higher priority, and they are not stored in the history log. The term ‘alarm’, when used in the Action column, means sounding and displaying a conforming audio-visual alarm.

A latching alarm is an alarm message that once generated will continue to display both the audible and visual elements, even though the original alarm condition has cleared. The user must acknowledge and un-latch the alarm, by pressing the ‘Alarm Mute’ button.

A non-latching alarm is an alarm message that will display both the audible and visual elements only during the alarm condition. If the alarm condition clears the audible and visual elements self-cancel.

The alarm messages below are ranked in order of priority. The current message of highest priority ranking is stored in the history log. Simultaneous lower ranking messages are often the consequence of a higher priority, and they are not stored in the history log (they will of course re-appear once the higher priority is resolved, if they still exist by then). The term ‘alarm’, when used in the Action column, means sounding and displaying a conforming audio-visual alarm.

Alarm message | Description | Action
(blank display) Simultaneous ‘Battery fail’ and ‘Mains disconnect’ | Total power loss. Battery has emptied (below 11.3v for more than 10 minutes), while in battery operating mode. Priority: HIGH Group: TECHNICAL Type: N/A Note: This follows a prolonged ‘battery low’ alarm (see below) | Ventilation stops (unsafe). Alarm sounder will continue for 10 seconds or until power is manually switched off.
‘Monitor Fail’ (shown in bottom Control LCD) | Hardware and/or software failure in Monitor. Cannot have confidence in ventilator operation. Priority: HIGH Group: TECHNICAL Type: LATCHING | Cannot be disabled. Remove ventilator from service.
‘Control Fail’ (shown in top Monitor LCD) | Hardware and/or software failure in Controller. Cannot have confidence in ventilator operation. Priority: HIGH Group: TECHNICAL Type: LATCHING | Cannot be disabled. Remove ventilator from service.
‘Gas Failure’ | Ventilator unable to reach any pressure. Gas supply not available. Priority: HIGH Group: TECHNICAL Type: LATCHING | Check supply. If supply is good, then remove ventilator from service.
‘High pressure’ | Patient circuit pressure exceeded 40mbar. Ventilator shut down its gas supply, but will make attempt to restart after 1 second (it could be a patient cough). Priority: LOW (for one off) Group: TECHNICAL Type: NON-LATCHING If the pressure exceeds 40mbar for a second time within 3 seconds (indicating a technical failure), then the gas will remain shut off. Priority: HIGH Group: TECHNICAL Type: LATCHING | The first alarm is non-latching. It is recorded in the history log. Second alarm is latching and gas supply will remain shut off. Operator must press ‘Alarm Mute’ button to restart ventilation. Examine patient circuit and exhalation valve for obstruction. Else, remove ventilator from service.
‘Circuit Failure’ | Ventilators cycles normally, but circuit pressure is not achieved. Assume accidental disconnection. Or, could be a manual intervention for a temporary normal medical procedure (e.g. suctioning). Priority: HIGH Group: TECHNICAL Type: NON-LATCHING | Examine patient circuit and exhalation valve for correct connections. If failure persists, remove ventilator from service.
‘Battery Low’ | Device is operating on battery power, and battery has <10% capacity remaining (approx. 10 to 20 minutes). Will not retrigger once acknowledged. Priority: MEDIUM Group: TECHNICAL Type: NON-LATCHING Is repeated as HIGH priority alarm 3 minutes before total shutdown. Will retrigger continually. Priority: HIGH Group: TECHNICAL Type: NON-LATCHING | Connect power supply. Check fuse in power supply. Replace if necessary. Alarm clears automatically when battery re-charges.
‘EP Below Set’ | EP is more than 2mbar below the set value, for more than 3 breaths. Priority: MEDIUM Group: TECHNICAL Type: NON-LATCHING | Examine patient circuit and exhalation valve for correct connections. If failure persists, remove ventilator from service.
‘EP Above Set’ | EP is more than the 2mbar above the set value, for more than 3 breaths. Priority: MEDIUM Group: TECHNICAL Type: NON-LATCHING | Examine patient circuit and exhalation valve for correct connections. If failure persists, remove ventilator from service.
‘IP Below Set’ | IP is more than 3mbar below the set value, for more than 3 breaths. Priority: MEDIUM Group: TECHNICAL Type: NON-LATCHING | Examine patient circuit and exhalation valve for correct connections. If failure persists, remove ventilator from service.
‘IP Above Set’ | IP is more than the 2mbar above the set value, for more than 3 breaths. Priority: MEDIUM Group: TECHNICAL Type: NON-LATCHING | Examine patient circuit and exhalation valve for correct connections. If failure persists, remove ventilator from service.
‘Tdi Too Long’ | Tdi exceeds 0.7s. Possible excessive circuit leak or a supply gas flow issue. Priority: MEDIUM Group: TECHNICAL Type: NON-LATCHING | Examine patient circuit and exhalation valve for correct connections. If failure persists, remove ventilator from service.
‘Tde Too Long’ | Tde exceeds 0.7s. Possible resistive obstruction in expiratory tube or exhalation valve, or soiled bacteria filer. Priority: MEDIUM Group: TECHNICAL Type: NON-LATCHING | Examine patient circuit and exhalation valve for correct connections.
‘No Power Supply’ | Power supply is interrupted. Priority: LOW Group: TECHNICAL Type: NON-LATCHING Does not repeat once acknowledged. | Continue on battery power. Connect power supply. Replace if necessary. Check fuse in power supply. Replace if necessary.

## Alarm visual and audible indicators

The unit produces three alarm tones, corresponding to priorities, High, Medium and Low.

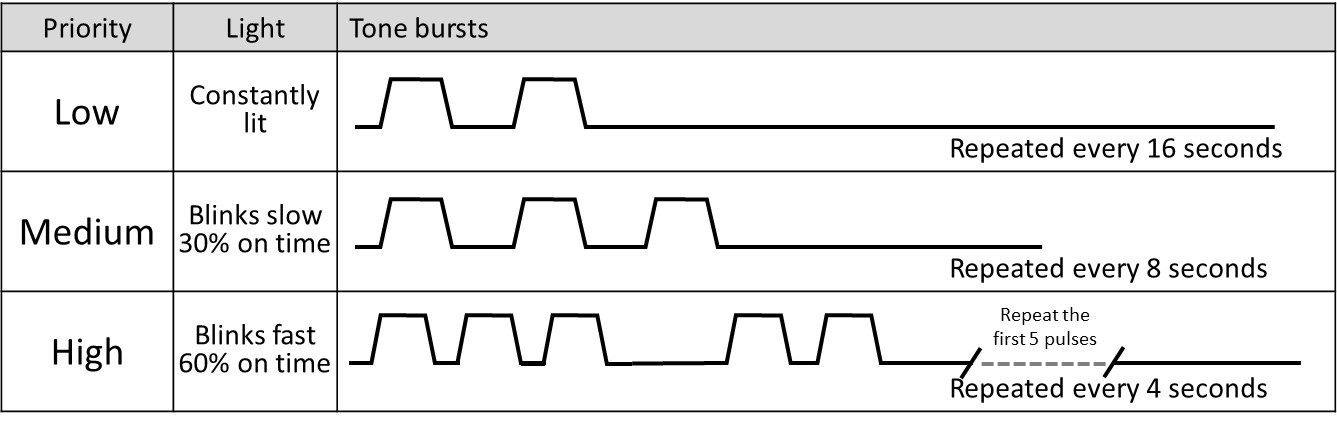
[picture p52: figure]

The pulsed tones are generated when the unit encounters an alarm condition. All the generated tone alarms are accompanied by visual alarm indication.

## Conditions that temporarily suspends the alarms

Condition | Action
Power-up | On power up, the ‘Gas Failure’ and all Medium priority alarms are suspended for 1 min that follows the self-test, to allow the system to settle.
Parameter change | On changing an EP and IP settings, the EP and IP related alarms are suspended for 10 seconds, to allow the system to respond to the change.

# 4 Functional testing

The ventilator can be tested with a test lung attached. It should be noted that a test lung does not necessarily have the resistance and compliance of a natural lung. Breath detection can be simulated by pulling on the test lung, to expand its volume.

# 5 Battery

The ventilator contains 1 sealed lead acid battery that can operate the unit for at least 45 minutes in the event of a mains power fail situation. The 45 minutes period is for a battery that is in a good condition.

If the ventilator has been used on battery power and it has been allowed to fully discharge the battery, then the battery can be described as being in a deep discharged state. If the unit is stored or placed out of service without recharging the battery, the deep discharged state can severely reduce the battery life. The damage is irreversible and the battery must be replaced.

# 6 Extended storage

If the ventilator is to be stored away for a period greater than 30 days and is not possible to charge the battery during this time, then the following procedure is recommended to prevent deep discharge damage to the battery:

- Remove the ventilator’s top cover.
- Disconnect the negative battery terminal and move it away from the battery.
- Tie a label to the ventilator to say the battery is disconnected.

# 7 Cleaning and disinfection

The pre-assembled patient circuit is intended for single-use. Patient contaminants do not reach any parts of the ventilator, other than the single-use patient circuit. Cleaning and disinfection is generally not required between patients.

All cleaning, disinfection and sterilizing of the ventilator should be carried out under the direction of the appropriate hospital authority procedures and standards.

Before cleaning or disinfecting the exterior of ventilator the following tasks should be performed:

- The power supply mains cable should be disconnected from the socket.
- Remove the patient circuit and bacterial filters. Discard any single-use items as per appropriate hospital authority guidelines.
- Disconnect the gas supply.

## Cleaning – recommended method

For cleaning use 3 clean, disposable, absorbent, non-shedding cloths.

i. Wipe clean with the first cloth using a hand warm water or a mild general purpose detergent solution. Do not overload the cloth with liquid.
ii. Remove the first water and/or detergent solution with the second cloth using water only. Do not overload the cloth with liquid.
iii. Wipe dry with the remaining cloth. Care should be taken to ensure that the driver gas ports are not blocked by any debris.

DO NOT insert any object in to the gas ports. This action may result in damage to the port. If the user believes there is a foreign object in a gas port, please refer the device to qualified service personnel for inspection and repair.

DO NOT allow moisture to enter the electronic module or its electrical sockets.

DO NOT steam autoclave any part of the ventilator or otherwise subject it to temperatures above 60°C.

DO NOT immerse any part of the ventilator into any liquid.

DO NOT use solvent-based cleaning agents on paint and label surfaces.

DO NOT use any abrasive cleaners on display and label surfaces.

## Disinfection – recommended method

Alcohols such as 70% isopropanol have some activity against bacteria and viruses. They should only be used after all visible surface dirt has been removed from the area to be disinfected.

For disinfection use two clean, disposable, absorbent, non-shedding cloths. Wipe clean with the first cloth using Alcohol (70% isopropanol). Wipe dry with the remaining cloth.

Disinfectants containing compounds similar to PHENOL or ALKYLAMINES (Glucorrotamine) are unsuitable.

# 8 Gas supplies

High pressure gas supply is required at 2.5 bar to 5 bar.

Air must be medical grade to ISO8573.1 Class 1.4.1 (minimum level of filtration).

Nominal inlet gas flow is 60 L/min. Peak inlet gas flow is less than 80 L/min.

# 9 Operating environment

Temp: 10-40 ºC.

Humidity: 0-90% (non-condensing).

# 10 Power requirements

Voltage: 13.5v

Power: 60 VA

Battery: 12V 2.1AH sealed lead acid.

Battery back-up: More than 45 minutes.

Battery charging: Full charge - Up to 8 hours

Fuse (Battery): 1 off T2.0A 250V

# 11 Dimensions

Size of ventilator: 280 mm W x 210 mm D x 106 mm H

Weight, without patient circuit: 2.5 kg

# 12 Connectors

Gas Output port: 22mm Male conical connector to ISO5356-1

Gas Return port (on exhalation valve): 22mm Male conical connector to ISO5356-1

Patient Pressure port (on ventilator): Non-conical barbed spigot

# 13 Classification of Medical Electrical System (via power supply unit)

Type of protection against electric shock: Class I.

Degree of protection against electric shock: Type B.

IPX rating IP44

Unit must be earthed.

# 14 Environmental storage conditions

When packed for transport or storage;

Ambient Temperature: -40°C to +70°C

Relative Humidity: 10% to 90% non-condensing

Atmospheric Pressure: 500 hPa to 1060 hPa

# 15 Product life cycle

The ventilator has a product life of 8 years from the date of manufacture. This excludes the main battery, which has an approximate 4-year life.

Solenoid valves should be replaced with new or overhauled valves every 10,000 hours, or every 2 years of regular use.

Apart from the battery, the ventilator and accessories do not contain any special hazardous components. No special precautions are required for their disposal. The device should be disposed of in accordance to the local WEEE (Waste Electrical and Electronic Equipment) guidelines.

At the end of its useful life this battery should be disposed of in accordance with local authority guidelines.

# 16 Maintenance and calibration

Functionally test and calibrate the ventilator at least every 3 months, or if there is reason to believe performance could have drifted:

- Attach a calibrated flow meter to the ‘Gas Output’ port. The flow meter should vent into ambient (no breathing circuit attached). Power up the ventilator (mute any alarming). Press and hold the ‘Breath’ button. Adjust the pressure regulator (PR), until the flow is 60L/min. Lock the pressure regulator.
- In a set up with a test lung and connecting a calibrated pressure measurement device, verify that the set ventilator pressure corresponds to actual measured pressure.
- In a set up with a test lung, manipulate the test system to cause the various alarm conditions described in section 3.2 above. Confirm the ventilator triggers them correctly.

Complete overhaul, including replacing worn labels, solenoid valves and battery (if required) should be performed every 2 years, or earlier if the ventilator is damaged.

# 17 EMC compliance

The ventilator’s electromagnetic compatibility was summarily assessed to meet the requirements of the following relevant standards:

EN60601-1-2

EN61000-3-2

EN61000-3-3

Guidance and manufacturer's declaration - electromagnetic emissions

The ventilator is intended for use in the electromagnetic environment specified below. The customer or the user of the Xenon Blender should assure that it is used in such an environment.
Emissions test | Compliance | Electromagnetic environment- guidance
RF emissions CISPR 11 | Group 1 | The ventilator uses RF energy only for its internal function. Therefore, its RF emissions are very low and are not likely to cause any interference in nearby electronic equipment.

RF emissions

CISPR 11

Class B

The ventilator is suitable for use in all establishments and may be used in domestic establishments and those directly connected to the public low-voltage power supply network that supplies buildings used for domestic purposes, provided the following mandatory warning is paid attention to:

Warning: This equipment/system is intended for use by healthcare professionals only. This equipment/ system may cause radio interference or may disrupt the operation of nearby equipment. It may be necessary to take mitigation measures, such as re-orienting or relocating the ventilator or shielding the location.
Harmonic emissions IEC 61000-3-2 _ | Class A
Voltage fluctuations/ flicker emissions IEC 61000-3-3 | Complies

# 18 Preparation of a new ventilator

Remove all transit packaging. Inspect the gas ports and proximal airway port for any packing material. Retain packaging for future storage or transportation use.

Remove the protective film.

Examine the ventilator for visual damage.

Allow the unit to acclimatize – i.e if the device has been stored in a cold or humid environment whilst in transit/storage, then wait at least 4 hours.

# 19 Pneumatic diagram

The Monitor and Controller operate independently, in parallel, observing each other (watchdogs). This assures the detection and alarming on any single failure mode. Both the controller and the monitor are capable of detecting an excess pressure (>40 mbar) and each can shut down the supply gas. This duality safeguards that compressed gas does not reach the patient circuit. All valves are NC (normally closed) types and will default to shutting off gas supply in case of total (battery) power failure.

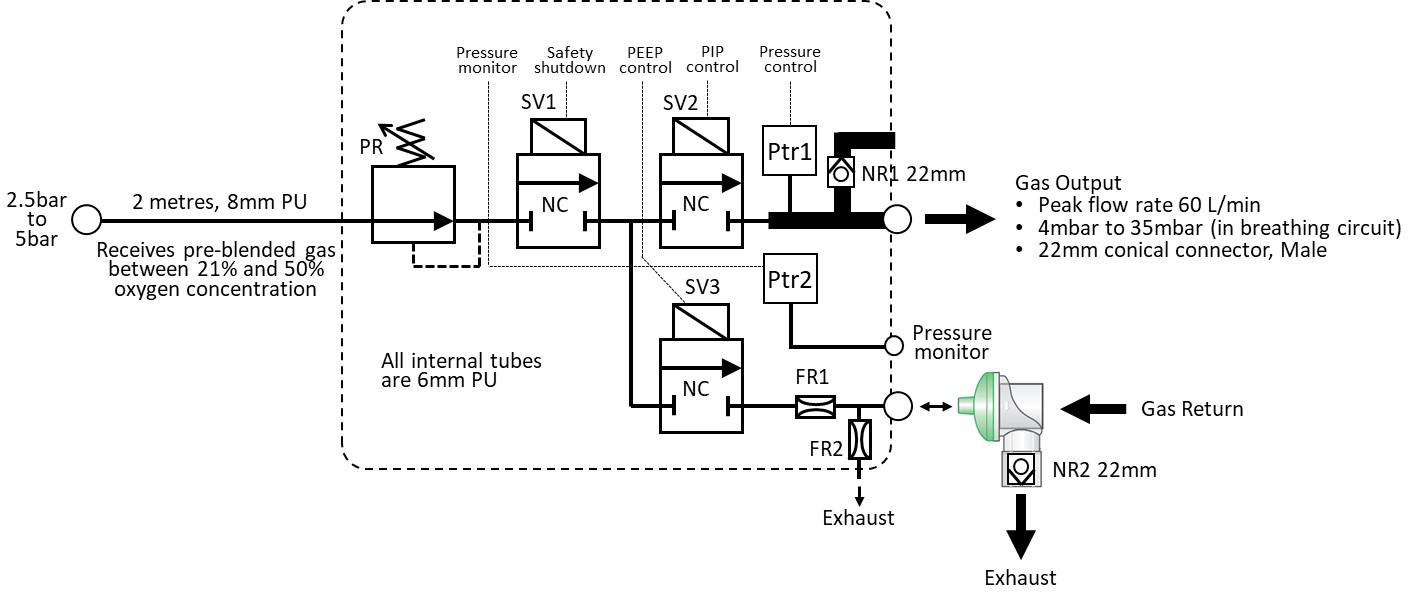
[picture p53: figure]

The Controller operates its own user interface, for adjusting the parameters (BPM, EP and IP). The Controller reports its 3 parameters values every 50mS to the Monitor. The Controller also reports when a valid change is made via the user interface. If the Monitor does not acknowledge receipt, then the Controller will instigate an alarm.

On shut-down, the patient can breathe ambient air through the 2 directional NR valves.

Overview flow diagram of ventilation cycle.


Note: When SV3 opens, then the Exhalation Valve closes. The short 50mS opening of SV2 tops up the IP or EP during the ‘hold’ phases, to compensate for any leak.

Trig.Rate = number of triggered breaths divided by total delivered breaths, over the last 50 breaths. The value is in effect averaged over the last 3 minutes approximately.

The Tdi measure the time from starting the inspiration cycle, until the IP plateau is reached. The displayed value is averaged for the last 20 breaths, to display a stable value. This averaging will still detect a natural, gradual drift.

The Tde measure the time from starting the expiration cycle, until the EP plateau is reached. The displayed value is averaged for the last 20 breaths, to display a stable value. This averaging will still detect a natural, gradual drift.

The breath detection looks for a real-time small pressure drop on the EP plateau pressure, which indicates the patient’s own inhalation work.

# 20 Serial data port

The data port is situated on the main PCB, inside the control unit enclosure. This feature is available for upgrading the ventilator software. The control unit enclosure should not be opened and the data port must not be connected to during clinical use.

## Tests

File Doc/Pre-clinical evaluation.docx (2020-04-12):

# Emergency Ventilator

# Pre-clinical evaluation

Issue/change record

Issue | Date | Author | Reason of issue/summary
0.A | 10/04/2020 | | DRAFT, released for ongoing development

# Introduction

This document contains the technical, usability and clinical evaluation of the Emergency Ventilator.

# 1 Method of evaluation

The physiological outcomes resulting from Pressure Controlled SIMV ventilation, when combined with blood gasses and vital signs monitoring, are well described. This is reflected in the choice of method for evaluating the Emergency Ventilator.

The pre-clinical evaluation is divided into two sections.

Section 2 introduces the clinical background and references established scientific literature, already affirming the efficacy Pressure Controlled SIMV. The section also identifies and addresses the clinical hazards associated with mechanical ventilation.

Section 3 is a device specific technical evaluation against the defined treatment and treatment specific safety parameters. This section makes reference to the technical validation and risk evaluation contained in ventilator’s design dossier.

Lastly, Section 4 concludes on the ventilator’s ability to meet clinical efficacy and safety.

# 2 Therapy validation

## 2.1 Intended use

Mechanical ventilation is indicated when the patient's spontaneous breathing is inadequate to maintain life. In general, mechanical ventilation is used to support the correct blood gasses and reduce the work of breathing. Mechanical ventilation provide assistance for breathing. It does not in itself treat the patients underlying ailment or disease.

The ventilator operates in conventional Pressure Controlled SIMV (Synchronised Intermittent Mandatory Ventilation) mode of ventilation only. It is intended for use with adult and young adult patients from 50kg and upwards. It interfaces with intubated, unconscious and semi-conscious, patients; and it interfaces with pressure ventilation masks on conscious patients.

The ventilator is designed for a simplified clinical protocol that demands minimal training and re-training. The gas cycling operation is designed to minimise oxygen consumption, to strictly what the patient requires. For purpose of simplicity, the I:E ratio (Inspiratory-Expiratory) is fixed 1:2. Inspiration flow rate fixed 60L/min, which produces an IP rise time of about 0.45s into a 600mL lung. The ventilator is intended for patients for whom this meets their therapeutic needs.

The general operating environment are hospitals and temporary healthcare facilities. Although the device is suitable for intra-hospital transport (moving patient between hospital departments, while being ventilated), it is not classed as a transport device. It is not designed for road or air transport.

## 2.2 Clinical risks

Although mechanical ventilation may prevent hypoxia or hypercarbia, resulting from a patient’s respiratory failure, it can also be damaging to the lungs.

The generic hazards related to the mode of treatment, and their initiating root causes, are illustrated here by a device independent fault tree. The initiating root causes are indicated by the boxes shaded in grey. The analysis considers the clinical hazards that are inherent in the ventilator, and excludes those inherent in the combination devices and medicines.

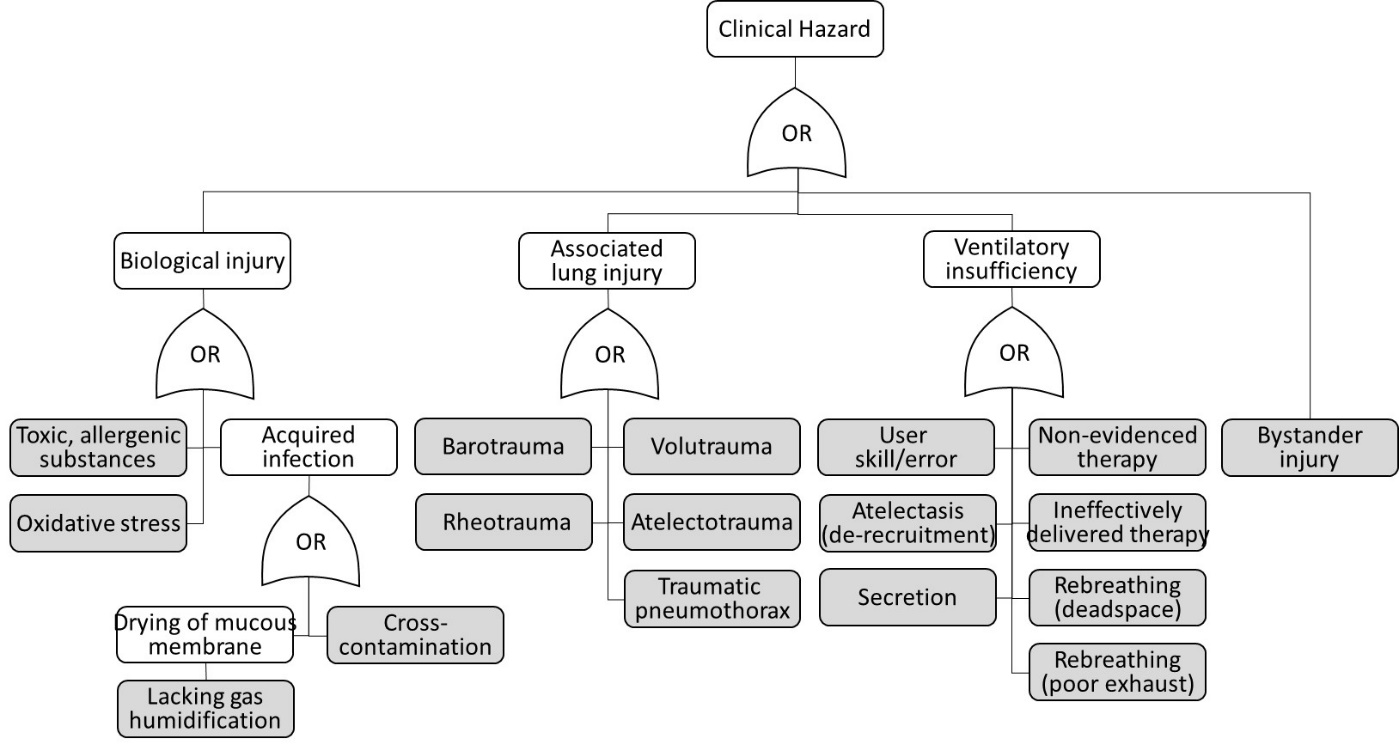
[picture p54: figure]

The initiating causes (boxes shaded in grey above) are addressed as follows:

### 2.2.1 Toxic, allergenic substances

This occurs from biologically incompatible substances entering the patient gas, either from the external gas supply system or from ventilator components.

It is recommended that the gas supply is medical grade and is monitored. The ventilator is designed for all components in the gas part being cleaned from any process substances.

### 2.2.2 Oxidative stress

This occurs when high concentrations of oxygen is delivered for a prolonged period of time. Oxygen is prescribed as a drug and it is the clinician’s responsibility to prescribe it prudently. The recommended technical system features monitoring to ensure that the prescribed concentration of FiO2 is being delivered, to an accuracy of 3% v/v.

### 2.2.3 Lacking humidification

It is recommended that a combination gas humidification device is used. See the User Instructions.

### 2.2.4 Cross-contamination

When the ventilator is used with an infectious patient, it is recommended to use a qualified bacteria on the exhaust port. The 22mm exhaust may also receive an adapter for connecting it to a scavenging system. See the User Instructions.

### 2.2.5 Barotrauma

The tension stress from an absolute pressure and/or shear stress on tissue that transmits a pressure can cause ruptures at the alveolar level.

The maximum inspiratory pressure (IP) is limited to 35mbar and the ventilator cuts gas supply at 40mbar. Although there is no generally accepted pressure at which there is no risk of barotrauma, the pressure range is comparably lower to other marketed ventilators. The risk of barotrauma is considered to be acceptably mitigated.

### 2.2.6 Volutrauma

Can occur by two mechanisms. 1) The tidal volume is inappropriately high, over-distending the lung as a whole; or 2) The tidal volume appears appropriate, but is disproportionately distributed to a recruited sub-part of the lung only. This can happen as result of a partial lung obstruction (e.g. by secretion) or from atelectasis (de-recruitment) in another part of the lung.

The maximum inspiratory pressure (IP) is limited to 35mbar. Although volutrauma can occur at 35mbar, standard clinical protocols advise clinicians to use the minimally necessary IP that achieves the desired blood gasses. Awareness and monitoring can acceptably manage the risk of volutrauma.

### 2.2.7 Rheotrauma

Similar to barotrauma, but where the stresses result from high gas flows.

The ventilator flow rate is limited to 60L/min, is comparably lower to the capabilities of other marketed ventilators.

### 2.2.8 Atelectasis and atelectotrauma

This relates to the alveoli collapsing between the breaths and lung tissue becoming is subject to mechanical shear stress when the lung is prised open. This can result in an inflammatory response or tissue damage.

The ventilator has an adjustable end-expiratory pressure (EP) which can be set to prevent the alveoli collapsing. It is recommended to use TcCO2 or EtCO2 monitoring, in which a decline in CO2 elimination would indicate atelectasis. See User Instructions.

### 2.2.9 Traumatic pneumothorax

An acute lung injury resulting from a pressure or flow ‘blast’, or from a significant over-distention of the lung.

The ventilator is limited to 40mbar maximum pressure. It has dual independent shutdown mechanisms, to prevent that any form of ventilator failure could result in a sporadic pressure spike.

### 2.2.10 User skill/error

The User Instructions defines the skill and responsibilities of the ventilator operator. The design has been simplified, to specifically lower the required user skills level.

Ventilator usability is subject to validation by the clinician testing.

### 2.2.11 Secretion

When a portion of alveoli are obstructed by secretion, then the lung function is reduced. It can also contribute to volutrauma, by the mechanism described in section 2.3.6 above.

It is recommended to monitor CO2 elimination and O2 saturation. A decline in any of these measures could indicate excessive secretion, which must be removed by suctioning. This is a standard practice in ventilation.

### 2.2.12 Non-evidenced therapy

Pressure Control SIMV is a well-known therapy dating back to the 1970’s. Accompanying this document are 2 example clinical review papers which demonstrate the clinical efficacy of Pressure Controlled invasive ventilation, including in the treatment of acute lung injury (ALI) or acute respiratory distress syndrome (ARDS). The papers acknowledge subtle differences between Pressure Controlled and Volume Controlled ventilation, but they do not identify any differences in patient outcomes of length of hospital stay.

a) Chacko B, et al. Pressure-controlled versus volume-controlled ventilation for acute respiratory failure due to acute lung injury (ALI) or acute respiratory distress syndrome (ARDS). Cochrane Database of Systematic Reviews 2015, Issue 1. Art. No.: CD008807. DOI: 10.1002/14651858.CD008807.pub2.
b) Garnero AJ, et al. Modos controlados por presión versus volumen en la ventilación mecánica invasiva. Med Intensiva. 2013;37:292-8. Study co-authored by Hospital Universitario del Henares, Coslada, Madrid.

Practically all currently marketed advanced ventilator feature Pressure Controlled SIMV modes of ventilation, including with volume control entirely disengaged, matching the clinical function of the present ventilator.

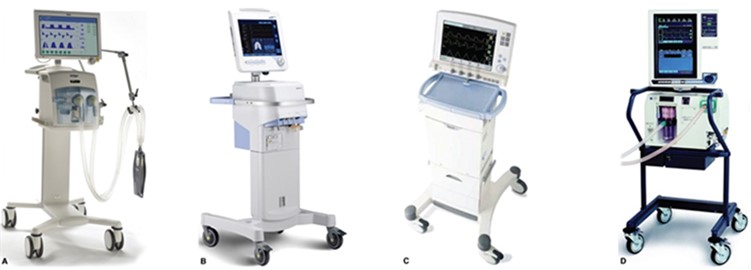
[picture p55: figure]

Examples of leading advanced ventilators that feature Pressure Controlled SIMV modes of ventilation. These advanced ventilators can operate with or without volume monitoring. The advanced ventilators of course also feature Volume Control and combination modes, which are above the function of the present ventilator. Their inclusion of Pressure Controlled SIMV nonetheless demonstrate its clinical validity.

### 2.2.13 Ineffectively implemented/delivered therapy

The risk is that the implemented pressure-flow profile is sub-optimal and does not make the gas exchange happen properly – i.e. the pressure plateau is too short or the tidal volume is insufficient, or EP is too high for the alveoli to fully empty.

Clinical protocols say that patients need between 4ml/kg and 8ml/kg volume (i.e. between 300ml and 600ml for a 75kg IBW person). This is a very wide range. Ventilation is therefore an output driven therapy. Blood CO2 level and O2 saturation are the outcomes. No one looks at a patient and prescribes a final volume or pressure. In practice, in Pressure Control ventilation, the clinician will start with a mid-range pressure. Then measures the blood gasses, which tells if there is a need to increase or decrease the pressure.

Of course, no one would want the pressure to result in so much volume that it over-stretches the lung (volutrauma). But no one would want to achieve a volume at any pressure either (barotrauma).

Another risk is that the ventilator inadequately synchronises with the patient’s spontaneous effort, resulting in Increased work of breathing or patient stress from ‘fighting’ the ventilator.

Both gas exchange and synchronisation are subject to validation by the patient trail.

### 2.2.14 Breathing circuit deadspace (rebreathing)

It is recommended to use a conformity assessed breathing circuit. See User Instructions.

### 2.2.15 Ineffective exhaust (rebreathing)

This has been subject to technical validations (see below) and is further subject to validation by the patient trail.

### 2.2.16 Bystander injury

The ventilator is conformity assess to the EC Medical Device Directive 93/42/EEC with regards to the safety and health of users or other persons coming into contact with the ventilator.

## 2.3 Patient trial result

To be completed.

Verify ability to maintain blood gasses (data or image of CO2 and O2 monitored values).

Verify patient comfort with the spontaneous breath synchronisation.

Describe conclusion of patient trial here, including any limitations.

Reference a competent clinical opinion.

# 3 Technical safety and performance validation

## 3.1 Technical implementation of Pressure Controlled SIMV

The present ventilator operates in Pressure Controlled SIMV (Synchronised Intermittent Mandatory Ventilation) mode of ventilation only. The mode secures a set number of breaths per minute, by firstly attempting to synchronize the mechanical delivery of breaths with patient’s spontaneous efforts. If the patient fails to spontaneously take a needed breath, then the ventilator delivers it mandatorily.

The ventilator reschedules the mandatory breath that follows a successfully synchronized spontaneous breath by 1 second. This is in anticipation that the patient will also instigate the following breath and to prevent a ‘fight’ between the patient and the ventilator.

SIMV behaves as PSV (Pressure Support Ventilation, including with reduced IP) when the patient makes full efforts, and it behaves as CMV (Continuous Mandatory Ventilation) if the patient does not make any efforts. When used with a mask on a conscious, spontaneously breathing patient, the SIMV behaves as nPSV or Synchronised BiPAP (by setting IP low). Switching the IP cycle off (or setting it equal to PEEP) makes SIMV behaves as CPAP (whether the patient is intubated or has a mask interface).

See User Instructions for the ventilation parameters.

## 3.2 Flow pressure waveforms

Insert images and measurement data here, to demonstrate the proximal flow and pressure waveforms.

Obtain a competent clinical opinion on the waveshapes.

## 3.3 Technical risks

Hazards related to the device technical system (component failure etc.) are mitigated by technical design. Device design dossier contains conformity assessments that evidence the ventilator meets requirements to European Medical Device Directive 93/42/EEC and the IEC 60601 (ISO 80601) series of standards on basic safety and essential performance of electrical medical equipment.

Risk Evaluation conforming to ISO 14971 on risk management of medical devices concludes that all known hazards are identified and their associated risks are reduced to acceptable levels. This conclusion relates to essential requirements for device safety, in respect of all current medical device standards.

See the design dossier.

## 3.4 User instructions

Contains the details specified in IEC 60601 (ISO 80601) series of standards, including warnings and precautions regarding residual risks.

## 3.5 Production quality assurance

See Production and Testing Specification in the design dossier, which outlines the response to production quality assurance requirements defined in the European Medical Device Directive 93/42/EEC.

## 3.6 Packaging

Packaging is specified to preserve and contain the ventilator during various modes of transport.

# 4 Conclusion

The Emergency Ventilator, subject to the user responsibilities and attention to the warnings described in the User Instructions, meets requirements for clinical efficacy and safety.

Title: Emergency Ventilator Date: 10 Apr 2020 Subject: Pre-clinical evaluation Issue: 0.A Doc No. [DRAFT] Page: 20 of 24

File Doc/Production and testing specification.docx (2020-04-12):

# Emergency Ventilator

# Production and test specification

Issue/change record

Issue | Date | Author | Reason of issue/summary
0.A | 10/04/2020 | | DRAFT, released for ongoing development

# Introduction

This document contains the quality assurance plan for producing the Emergency Ventilator design.

# 1 General quality assurance requirements

Council Directive 93/42/EEC, which remains current (while the MDR is under consideration for postponement), Annex V on production quality assurance requires:

The manufacturer, who is the entity who places their brand name on the ventilator, must ensure the following:

- The product is made in ways that it conforms to the approved design.
- The manufacturer’s quality system must be documented in a systematic and orderly manner in the form of written policy statements and procedures that are not open to misinterpretations. It must include in particular an adequate description of:
a) The manufacturer's quality objectives;
b) The manufacturer’s:
- Organizational structures, the responsibilities of the managerial staff and their organizational authority where manufacture of the products is concerned.
- Methods of monitoring the efficient operation of the quality system and in particular its ability to achieve the desired quality of product, including control of products which fail to conform.
- Methods of monitoring the efficient operation of sub-contractors and in particular the type and extent of quality system controls applied to the third party.
c) Inspection and quality assurance techniques at the manufacturing stage and in particular:
- Processes and procedures which will be used, particularly as regards sterilization, purchasing and the relevant documents.
- Product identification procedures drawn up and kept up to date from drawings, specifications or other relevant documents at every stage of manufacture.
d) Appropriate tests and trials to be carried out before, during and after manufacture, the frequency with which they will take place, and the test equipment used; it must be possible adequately to trace back the calibration of the test equipment.
- Keep up to date a systematic procedure to review experience gained from devices in the post-production phase and to implement appropriate means to apply any necessary corrective action.
- Notify the national ‘Competent Authorities’ of the following incidents immediately on learning of them:
i. Any malfunction or deterioration in the characteristics and/or performance of a device, as well as any inadequacy in the labelling or the instructions for use which might lead to or might have led to the death of a patient or user or to a serious deterioration in his state of health.
ii. Any technical or medical reason connected with the characteristics or performance of a device for the reasons referred to in subparagraph (i) above leading to a systematic recall of devices of the same type by the manufacturer.

In usual times, for products marketed within the EU/EEA, the manufacturer must submit the quality systems and design dossier to assessment and periodic surveillance by a Notified Body. The manufacturer must inform the notified body which approved the quality system of any plan for substantial changes to the quality system. This requirement may be deferred in time of a pandemic emergency (check your national regulatory authority’s position).

# 2 Components procurement

## 2.1 Specifying and purchasing components and services

Ensure that goods or service requirements, are fully and unambiguously specified – to reduce the risk of inadvertently receiving the wrong or sub-standard parts.

Ensure the supplier receives the latest drawings of fabricated parts. Where a document has been revised, ask the supplier to confirm that they have disposed of the outdated revision.

Where available, request a certificate of conformity.

Where deliveries were incomplete or had a discrepancy against what was orders, the issue will be resolved with the supplier, prior to putting the components into use.

Recorded evidence of receipt and status (inspection result, accepted or rejected) of ordered goods or services. On occasions, a discrepancy or other issue may not become apparent until the product is put into use. It is important to be able to obtain the suppliers commitment to correct the issue at the soonest possible.

## 2.2 Traceability

Maintain traceability records of critical components – from purchasing orders, through warehousing, to production and product delivery – to enable locating and recalling any components that are subsequently to have a quality problem. Remember, the product is a life-support ventilator.

It cannot be tolerated that a ventilator operates with the risk of a known defect being realised. Even if it is not possible to replace a degraded component immediately, it must be possible to at least notify the user that a risk exists – to enable them prepare a backup response to the possible failure.

See the record sheet Appendix.

## 2.3 Stocking parts

Maintain storage conditions in accordance to the manufactures’ recommendations.

Generally, use a first-in-first-out (FIFO) picking method, to ensure stock turn over and best manage any shelf-life implications.

# 3 Assembly

## 3.1 Electronic sub-assembly

To be determined and described in outline terms. Add pictures illustrating important details.

It may be appropriately to produce a test jig at this stage – in particular if the sub-assembly is made by a sub-contractor.

## 3.2 Pneumatic sub-assembly

To be determined and described in outline terms. Add pictures illustrating important details.

Record serial and batch number information in the inspection, testing and release record (see Appendix).

It may be appropriately to produce a test jig at this stage – in particular if the sub-assembly is made by a sub-contractor.

## 3.3 General assembly

To be determined and described in outline terms. Add pictures illustrating important details.

Pneumatic tubes and electric wires are routed orderly and securely. Tie or fasten at appropriate points, to ensure no item is snagged or could move to become snagged or rubbed. [add picture]

Leave the ventilator in default calibration settings.

## 3.4 Burn-in

Operate the ventilator on air for 24 hours non-stop and maximum parameter settings. Remove the top cover during the burn-in, to be able to observe and measure any concerns.

There is no need to accurately calibrate the ventilator, prior to the burn-in. Some brand-new components, including pressure regulators and solenoid valves, will ever so slightly drift in their first 24 hours of operation – e.g. solenoid valve response time tends to improve very slightly.

Between 8 and 12 hours of burn-in, remove the power cord and let the ventilator run down its battery. Verify the battery delivers at least 45 minutes of operation. Measure and record the battery voltage after 45 minutes.

# 4 Inspection and calibration

## 4.1 Inspection

Visually verify that all pneumatic tubes and electric wires are routed orderly and securely. No item is snagged or could move to become snagged and wear.

Visually verify that all fasteners (screws, clips, ties) are correctly placed and securely made.

Visually check that when observed at 30cm distance, using a normal uncorrected or corrected vision, that the ventilator is free from detracting marks.

Visually verify that the ventilator has all the correct labels and that they are securely attached.

## 4.2 Calibration

To be determined and described.

## 4.3 Final testing

To be determined and described.

Using testing tools, verify each alarm function in turn.

If, as result of failing the first testing, the ventilator is reworked, then the final testing must be repeated in full.

# 5 Release approval

The person who the manufacturer has designated authority to release the products, must verify that the Inspection, Testing and Release Record (see Appendix) for:

a) Ventilator identification is correctly recorded.
b) All traceability details are properly recorded.
c) Appropriateness of any concession items.
d) Test records demonstrate that the ventilator conforms to the test specification.
e) That any rework information is recorded and has resulted a final testing in full.

The authorised person signs the correctly completed document, to approve the ventilator’s release into the market.

# Appendix – Inspection, testing and release record

Emergency Ventilator 2020
Ventilator serial number:
Hardware revision number:
Software revision number:
Inspector’s initials:

Part ID | Description | Batch/serial number
PCB | Pre-assembled, pre-tested PCB with pressure transducers
PR | Pressure regulator <model number>
SV1 | Solenoid valve <model number>
SV2
SV3
PTR1
PTR2
PSU
Battery

Concession items

Test and measurement equipment | ID | | Calibration date
Flow meter
Pressure sensor
Voltage meter
Test parameter | | Target | | Measured
Battery operation time | | Minimum 45 min
Total power fail alarm voltage | | 11.5v
Battery charging voltage after 6 hours
Test point 1 voltage | | 5V (+/- 0.15)
Inspiration flow rate from ‘Gas Output’ port | | 60L/min (+/-2)
Volume calculation, when delivering 450ml (+/-25) | | Max error 15ml
Pressure accuracy
Test each alarm trigger and message | | Target | | | Met/Not met
‘Circuit Failure’ – disconnect test lung
‘EP Below Set’ – pinche/clamp pressure sense tube
‘EP Above Set’ – clamp pressure tube and compress
‘IP Below Set’ – pinche/clamp pressure sense tube
‘IP Above Set’ – clamp pressure tube and compress
‘Tdi Too Long’
‘Tde Too Long’
‘High pressure’
‘Gas Failure’
‘No Power Supply’ – unplug power supply
‘Battery Low’ – reduce voltage by variometer. Cancel alarm when sounding. | | MP alarm at 11.7v (+/- 0.1). No alarm repeat.
Total power fail – reduce voltage by variometer | | HP alarm at 11.3v (+/- 0.1v). Auto shut down after 3 min.
‘Monitor Fail’ – short circuit monitor MPU crystal.
‘Control Fail’ – short circuit monitor MPU crystal.
Visuals | | Target | | | Met/Not met
Labels and markings | | As per drawing
Free from marks and blemishes | | None, viewed at 30 cm

Details of any rework and re-inspection

Release approval
Approver initial
Approver signature
Date

Title: Emergency Ventilator Date: 10 Apr 2020 Subject: Production and test specification Issue: 0.A Doc No. [DRAFT] Page: 20 of 24

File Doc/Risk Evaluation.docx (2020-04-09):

# Emergency Ventilator

# Risk Evaluation

Issue/change record

Issue | Date | Author | Reason of issue/summary
0.A | 05/04/2020 | | DRAFT, released for ongoing development

# 1 Device

The device is a ventilator intended for providing mass intensive respiratory care, in facilities that might be lacking in full hospital infrastructure, abundant oxygen supplies and clinical experiences – such as under pandemic emergency conditions.

The ventilator is designed for a simplified clinical protocol that demands minimal training and re-training. It is further designed to be mass-producible and requiring minimal maintenance. The gas cycling operation is designed to minimise oxygen consumption.

The ventilator uses conventional Pressure Controlled SIMV (Synchronised Intermittent Mandatory Ventilation) mode of ventilation only. It interfaces with intubated, unconscious and semi-conscious, patients; and it interfaces with pressure ventilation masks on conscious patients. There is no need to select and switch between alternative modes or interfaces.

SIMV behaves as PSV (Pressure Support Ventilation) when the patient makes full efforts, and it behaves as CMV (Continuous Mandatory Ventilation) if the patient does not make any efforts. When used with a mask on a conscious, spontaneously breathing patient, the SIMV behaves as nPSV or Synchronised BiPAP (by setting IP low). Switching the IP cycle off (or setting it equal to PEEP) makes SIMV behaves as CPAP (whether the patient is intubated or has a mask interface).

For purpose of simplicity, the I:E ratio (Inspiratory-Expiratory) is fixed 1:2. Inspiration flow rate fixed 60L/min, which produces an IP rise time of about 0.45s into a 600mL lung.

The device is not intended to be marketed as a commercial medical device. The device conforms to medical device requirements for basic safety and essential performance. There is not, yet, any basis for proving the clinical efficacy of the device.

The ventilator is designed to operate in combination with an external power supply, a breathing circuit and a respiratory gas humidifier (HME or water chamber).

## 1.1 Intended use

The ventilator is intended for use with adult and young adult patients from 50kg and upwards. It interfaces with intubated, unconscious and semi-conscious, patients; and it interfaces with pressure ventilation masks on conscious patients.

The device is intended to be operated and maintained by rapidly trained, lesser confident intensive care personnel – oversee by expert respiratory therapists.

The general operating environment are hospitals and temporary healthcare facilities. Although the device is suitable for intra-hospital transport (moving patient between hospital departments, while being ventilated), it is not classed as a transport device. It is not designed for road or air transport.

The risk management plan considers environmental exposures that can occur during normal conditions of use, shipping and storage. It covers the complete life-cycle of the device and assumes that a mandatory level of maintenance is performed.

# 2 Risk management plan

The plan and risk management activities are performed in conformance to the current revision of ISO14971 on the application of risk management to medical devices, including the information guidance published with this standard. Specific documented company processes for risk management, providing more details on inputs and outputs for particular activities, are integrated into the company quality management system. This plan requires adherence to the ISO14971 standard and the documented company processes.

## 2.1 Responsibility and authority

The overall responsibility for safety and performance of company products rests with the board of directors of the manufacturer whose brand name appears on the ventilator. The responsibility and authority for device risk management is delegated to the organisations Quality and Regulatory Affairs Manager, who will ensure this plan and its associated activities are effectively implemented and maintained.

The organisation’s senior management team is delegated responsibility for receiving and reviewing summary reports on device risk management activities, to verify their completeness, effectiveness and to take corrective action on any shortfall. The senior management team will ensure that risk management activities are sufficiently and competently resourced. The quality management system incorporates documented process for management review, including the recording of decisions and actions.

The product development process incorporates parts of the risk management process (e.g. the process for this document). Individual design engineers are responsible for ensuring that this process is appropriately implemented during the development project, which will include requirements for conformance with recognised (harmonized) safety and performance standards; and that devices are not released into the market prior to have undergone a risk evaluation and review in accordance with requirements set out in this plan.

## 2.2 Requirements for review

The risk acceptance criteria, analysis, evaluation and controls for the device are reviewed in accordance with the documented organisational process for product risk management, which is at least annually or following any event that draws the current controls into question. A review triggered by the latter reason, may be limited in scope to the systems potentially affected.

Risk management review will consider information available in records and determine whether any:

a) Previously unrecognised hazards are present;
b) Previous conclusion concerning acceptability of risks remains valid;
c) Previous conclusion concerning acceptability of residual risks remains valid.

Results of the evaluation process are recorded in the risk management file, including:

a) Degree of effectiveness of the risk analysis and controls for the device;
b) New controls and/or actions required to reduce risk or to assure that risk is maintain at a specified acceptable level;
c) New user information required concerning residual risks.

The organisation’s senior management team will periodically receive and review summary reports as follows:

a) Monthly on any open adverse incidents, including actions and progress;
b) Quarterly summary of device risks situation, compared to objectives set out in this plan;
c) Outcomes of risk management reviews, at the earliest opportunity after their occurrence.

## 2.3 Methodology for obtaining information for reviews

The quality management system incorporates documented processes for dealing with device safety issues in a systematic manner, including:

a) Incorporating basic safety requirement from harmonized international standards – i.e. the IEC 60601 (ISO 80601) series of standards on medical electrical equipment.
b) Maintaining production traceability of safety critical parts; and recording outcomes of inspection and testing, including software validation (PEMS). Every individual device is subjected to 100% final inspection and testing. Any deviance from intended performance is recorded.
c) Receive, record and handle adverse incidents, including processes for Corrective and Preventive Action, Advisory Notices and Recall.
d) Receive, record and monitor general market feedback concerning performance in the field.
e) Post-introduction market surveillance for input into the ongoing products planning and specification process, including appraisals of strengths, weaknesses and trends in state-of-art in similar devices in the market. Areas of search include relationships with market drivers (medical practitioners), user visit reports, trade fairs, and competitor products reviews.

Information relating to new or revised standards is obtained through:

a) Notified Body surveillance and advanced updates
b) Government publications.

## 2.4 Methodology for risk analysis

Available information and sources of information will be systematically used to identify and estimate the risk of the anticipated sources of harm associated with the device. Information includes testing and validation data, including from the Programmable Electrical Medical Systems (PEMS) validation.

The analysis considers internal (self) sources and environmental (external) sources and causes. The scope of analysis includes intended use and any likely and reasonably foreseeable misuse.

The identification will consider:

a) Is there a source of harm?
b) Who is most vulnerable to the harm?
c) How could the hazard occur?

The information is used to estimate the reasonably foreseeable sequence of events that could result in a hazardous situation. Where certain aspects are unknown, the analysis will involve seeking out missing information, in order to be able to qualify/quantify the risk. All identified risks are recorded.

Where established knowledge confirms that it would be impossible for a certain hazard being realised, then the particular aspect is, by definition, not a risk and it should not necessitate any further evaluation.

## 2.5 Criteria for risk acceptability

Risk acceptability is based on a rating of the probability of occurrence of harm and severity of the consequence of that harm. The rating may be weighed or influenced by recognized standards and/or perception factors – in the context of the particular markets.

The context is that candidate patients for life-supporting ventilation are either deeply unconscious or have compromised lung function or strength, or both, and would be unable to sustain own breathing over time. Patient monitoring provides clear indication of effectiveness of treatment and whether patient is in immediate danger of respiratory failure.

The alternatives to the simplified approach to ventilation provided by this device, is to move the patient to a more advanced intensive care unit, where more advanced respiratory care resources exist. However, such resources can be insufficient in times of a widespread pandemic. The device subject to this assessment fill an essential gap in the needs to treat patients. The alternative is unviable.

Ventilation is an output-based therapy and involves a large degree of variability in clinical application, skills and judgement. The important aspects for the device are that it performs reliably and accurately, with relevant and timely information feedback to the user.

Table 1: Definition of probability of occurrence of harm

Frequent | 1 occurrence in every 5 device operating days, or every 1 patient treatment sessions
Probable | 1 occurrence in every 50 device operating days, or every 12 patient treatment sessions
Occasional | 1 occurrence in every 500 device operating days, or every 125 patient treatment sessions
Remote | 1 occurrence in every 5,000 device operating days, or every 1,250 patient treatment sessions
Improbable | 1 occurrence in every 50,000 device operating days, or every 12,500 patient treatment sessions
Almost impossible | 1 occurrence in every 500,000 device operating days, or every 125,000 patient treatment sessions

Assumptions and context:

- Average patient treatment session is 5 days
- Average number of sessions per year per device is 60 patients
- Number of ventilator operating days per year per device is 160 days
- Estimated market life of device design is 15 year, of which 14 years is in non-use storage.
- Total number of devices in the market is 10,000 units
- Total number of patients exposed to all devices over the market life of the device design is 600,000 patients, during emergency situations over the 15 years device life (used 1 year).
- Total number of device operating days over the market life of the device design is 3 million days, over 10 years when the device is only used intermittently for a combined 1 year.
- Ventilation therapy involves significant variability in clinical application, skills and judgement, which has a bearing on the quality of patient outcomes with any given device.

Table 2: Definitions of consequences of harm

Catastrophic | Potential for resulting in death or multiple deaths
Critical | Potential for resulting in permanent non-trivial impairment or life-threatening injury
Serious | Potential for injury or impairment requiring additional professional medical intervention.
Minor | Potential for temporary injury or impairment not requiring additional professional medical intervention.
Negligible | Results in inconvenience or temporary discomfort

Persons to be considered as possibly affected are patients, clinical personnel (users of the device), hospital technical and cleaning personnel, device manufacturer’s service personnel, relatives and any other visitors who could potentially come into contact with the device.

Table 3: Risk rating, by classifying probability and consequence of harm

Probability of occurrence of harm | Consequence of harm
| Negligible | Minor | Serious | Critical | Catastrophic
Frequent | 15 | 10 | 6 | 3 | 1
Probable | 19 | 14 | 9 | 5 | 2
Occasional | 24 | 18 | 13 | 8 | 4
Remote | 27 | 23 | 17 | 12 | 7
Improbable | 29 | 26 | 22 | 16 | 11
Almost impossible | 30 | 28 | 25 | 21 | 20

Where review and sound reasoned judgement establishes that it would be practically impossible for a harm being realized (i.e. it figures below the range of probability), then the particular aspect is, by definition, not a risk and it should not necessitate any further consideration

Table 4: General interpretation of risk acceptability

Risk rating | Risk acceptability | Action, in general
1 – 6 | Intolerable | Devices should not be placed in the market, until risk is reduced to a tolerable level. Any existing users in the field must be notified urgently. Establish fastest possible time period for any field corrective action. Generally, any field device should be withdrawn from use.
7 – 15 | Moderate | Devices should not be placed in the market, until risk is reduced to a tolerable level. Any existing users in the field must be notified at the earliest practical time. Establish fastest practical time period for any field corrective action. Urgent user information and action required, if associated with a potentially ‘catastrophic’ consequence.
16 – 24 | Tolerable | Efforts should be made to reduce the risk, where benefits of the solution outweigh the disruption and cost of implementation – in respect of the influencing factors described below. A time period should be defined for implementation. Monitoring is required to ensure that any established controls are maintained.
25 – 30 | Negligible | Additional controls are generally not required. Monitoring is required to ensure that any established controls are maintained.

The interpretation of risk acceptability in table 4 is a general one. The final acceptance and action for a particular risk may be influenced by the following factors:
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

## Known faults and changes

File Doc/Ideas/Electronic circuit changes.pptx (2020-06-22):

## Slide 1

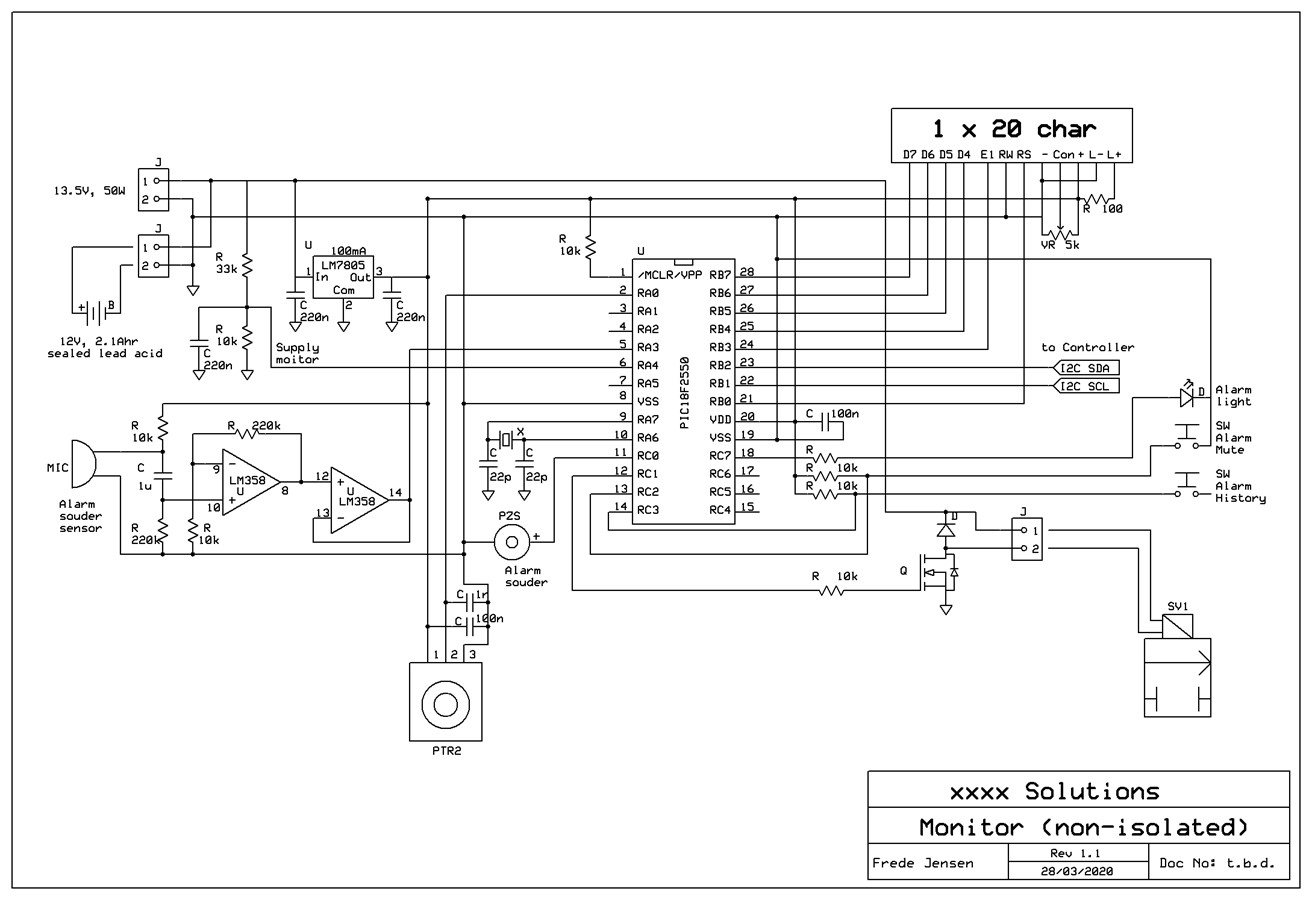
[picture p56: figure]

Monitor circuit diagram:
Added power voltage monitor:
- < 13v = PSU disconnected (low priority alarm)
- < 11.7v = battery low (medium priority alarm)
- < 11.3v = safety shutdown in 3 min (high priority alarm)
Change to 5v MPU. The initially suggested PIC model operates on 1.8v to 3.6v, which is incompatible with most LCDs.
Increased FET gate resistor to 10k. This slightly slows the FET switching time (without out causing heating) and better isolates/protects the MPU from the higher power circuit.
Changed LCD to 20 characters, to display a tidal volume value.

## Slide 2

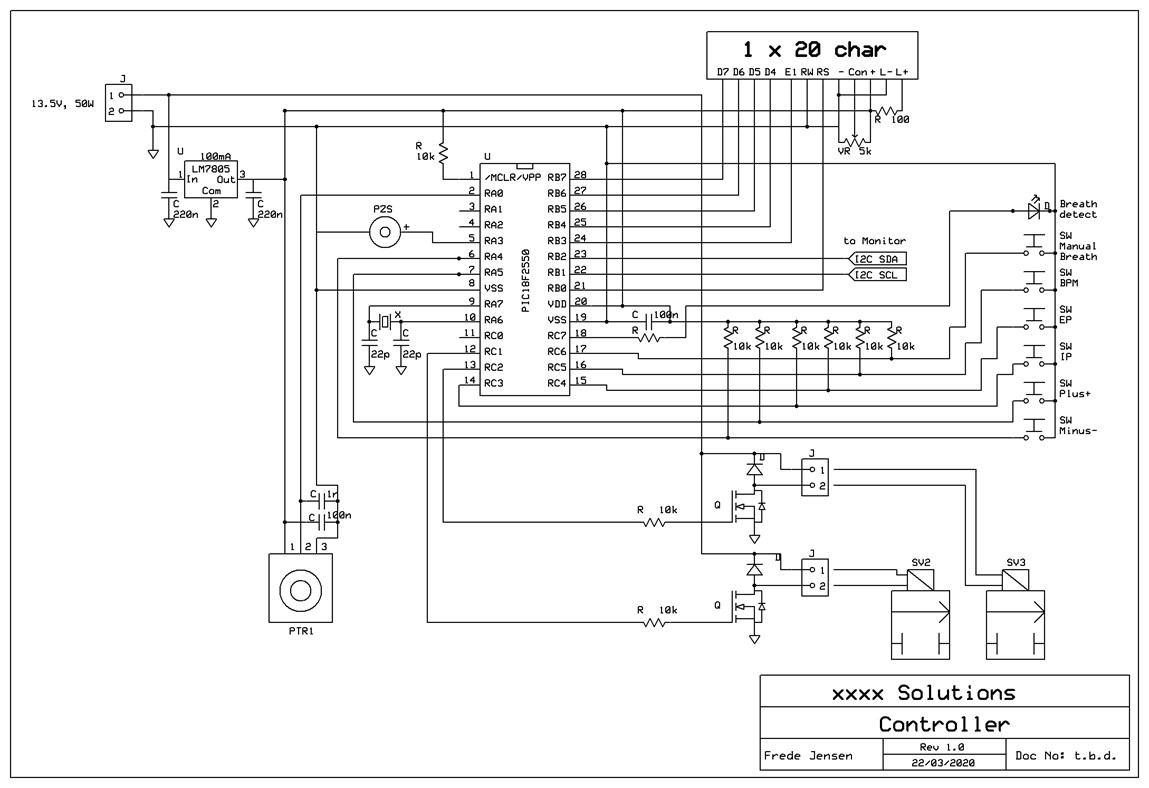
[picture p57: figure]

Controller circuit diagram:
Change to 5v MPU. The initially suggested PIC model operates on 1.8v to 3.6v, which is incompatible with most LCDs.
Increased FET gate resistors to 10k. This slightly slows the FET switching time (without out causing heating) and better isolates/protects the MPU from the higher power circuit.
Changed LCD to 20 characters, to match the Monitor unit and leave opportunity for introducing a Minute Volume parameter.

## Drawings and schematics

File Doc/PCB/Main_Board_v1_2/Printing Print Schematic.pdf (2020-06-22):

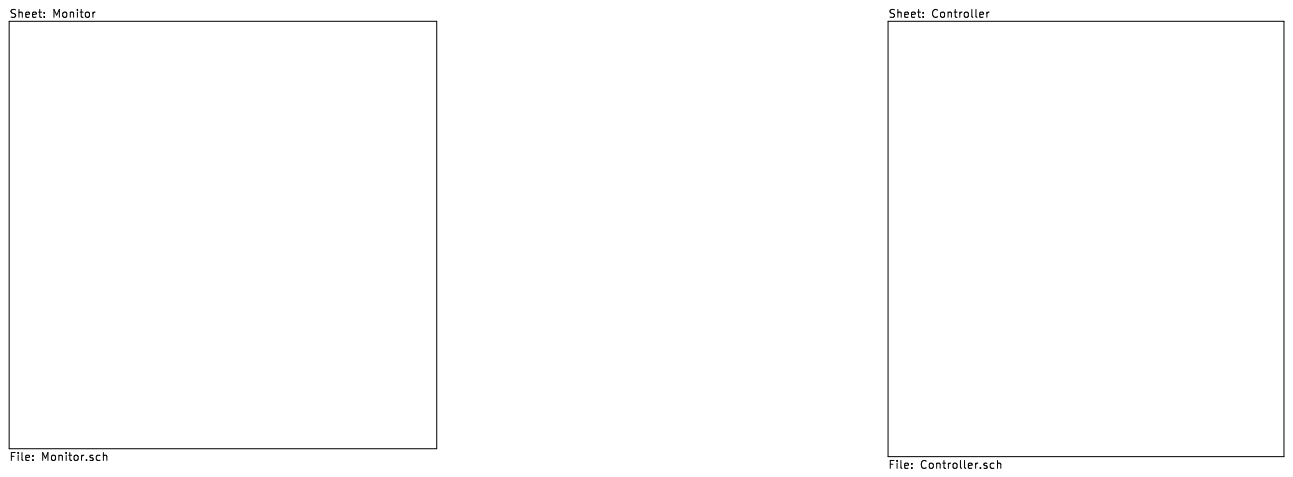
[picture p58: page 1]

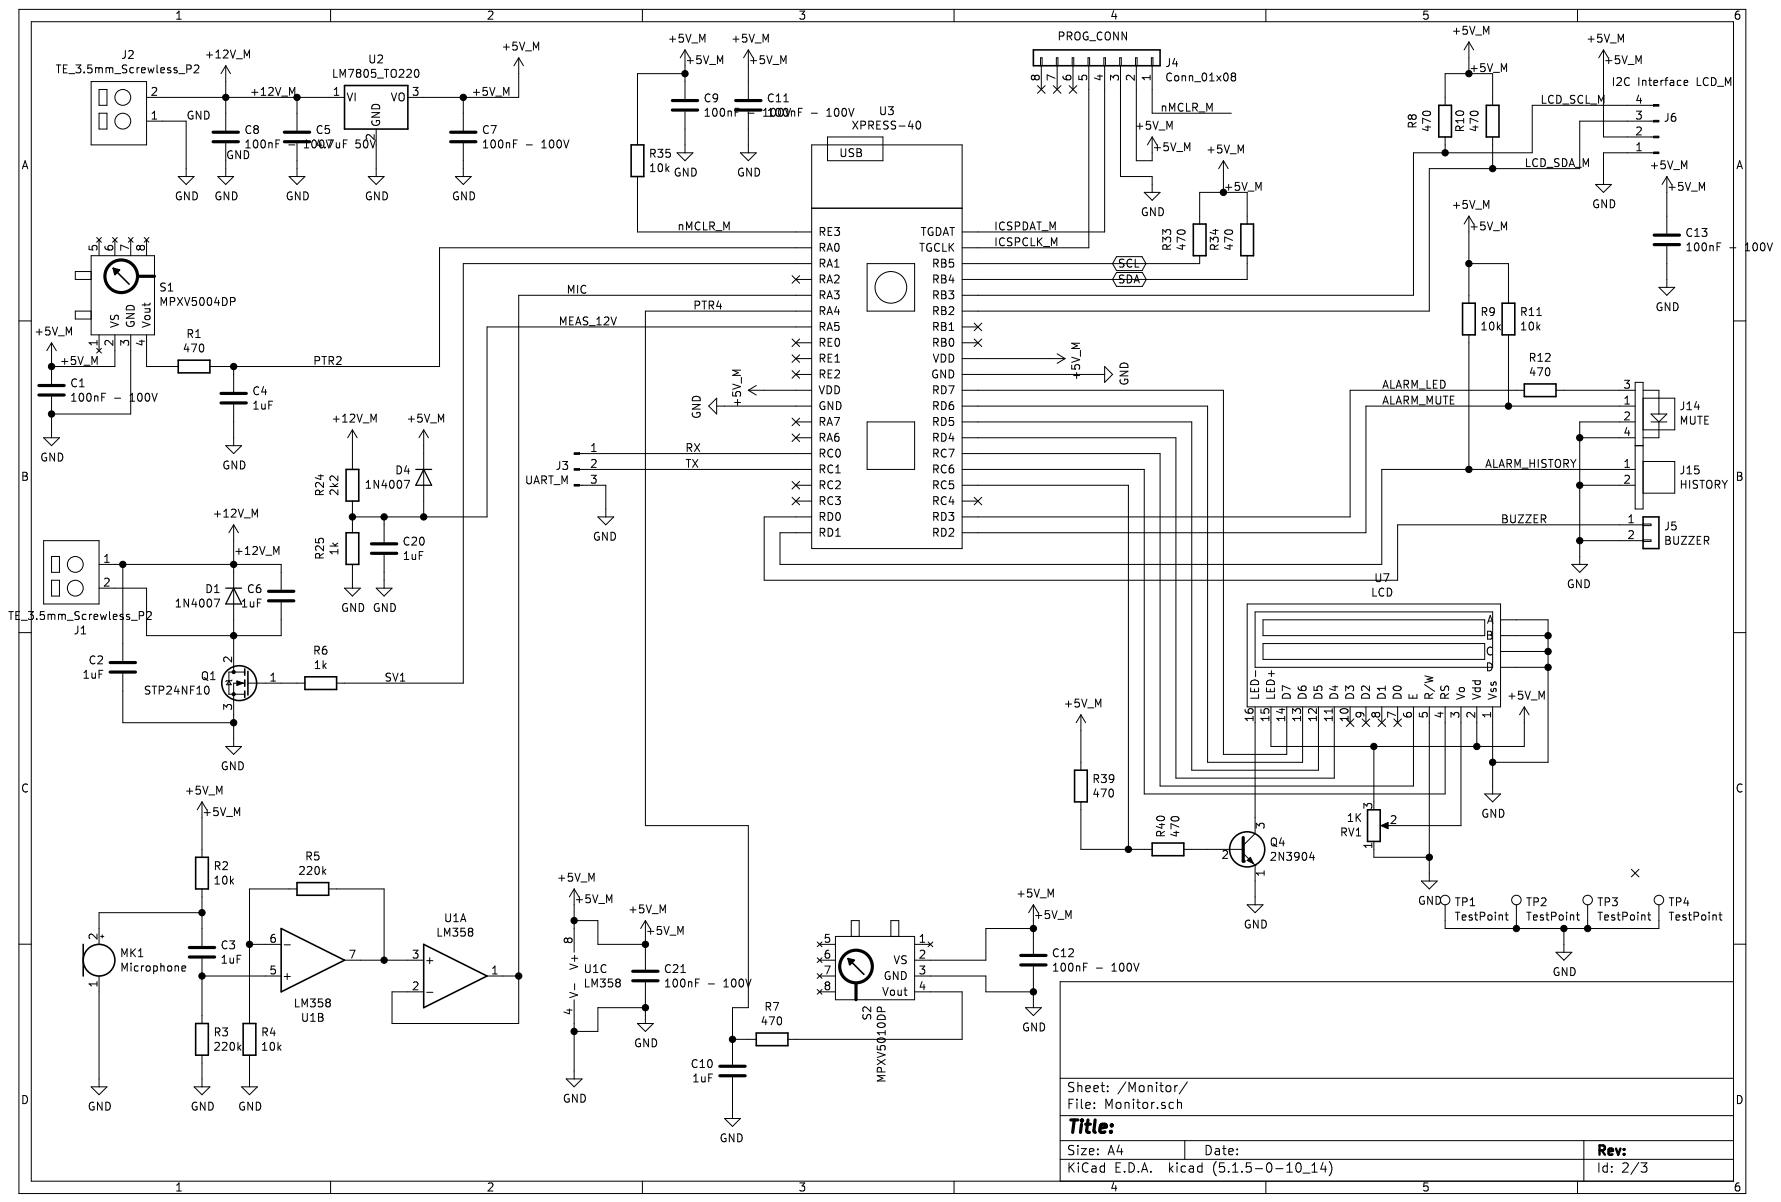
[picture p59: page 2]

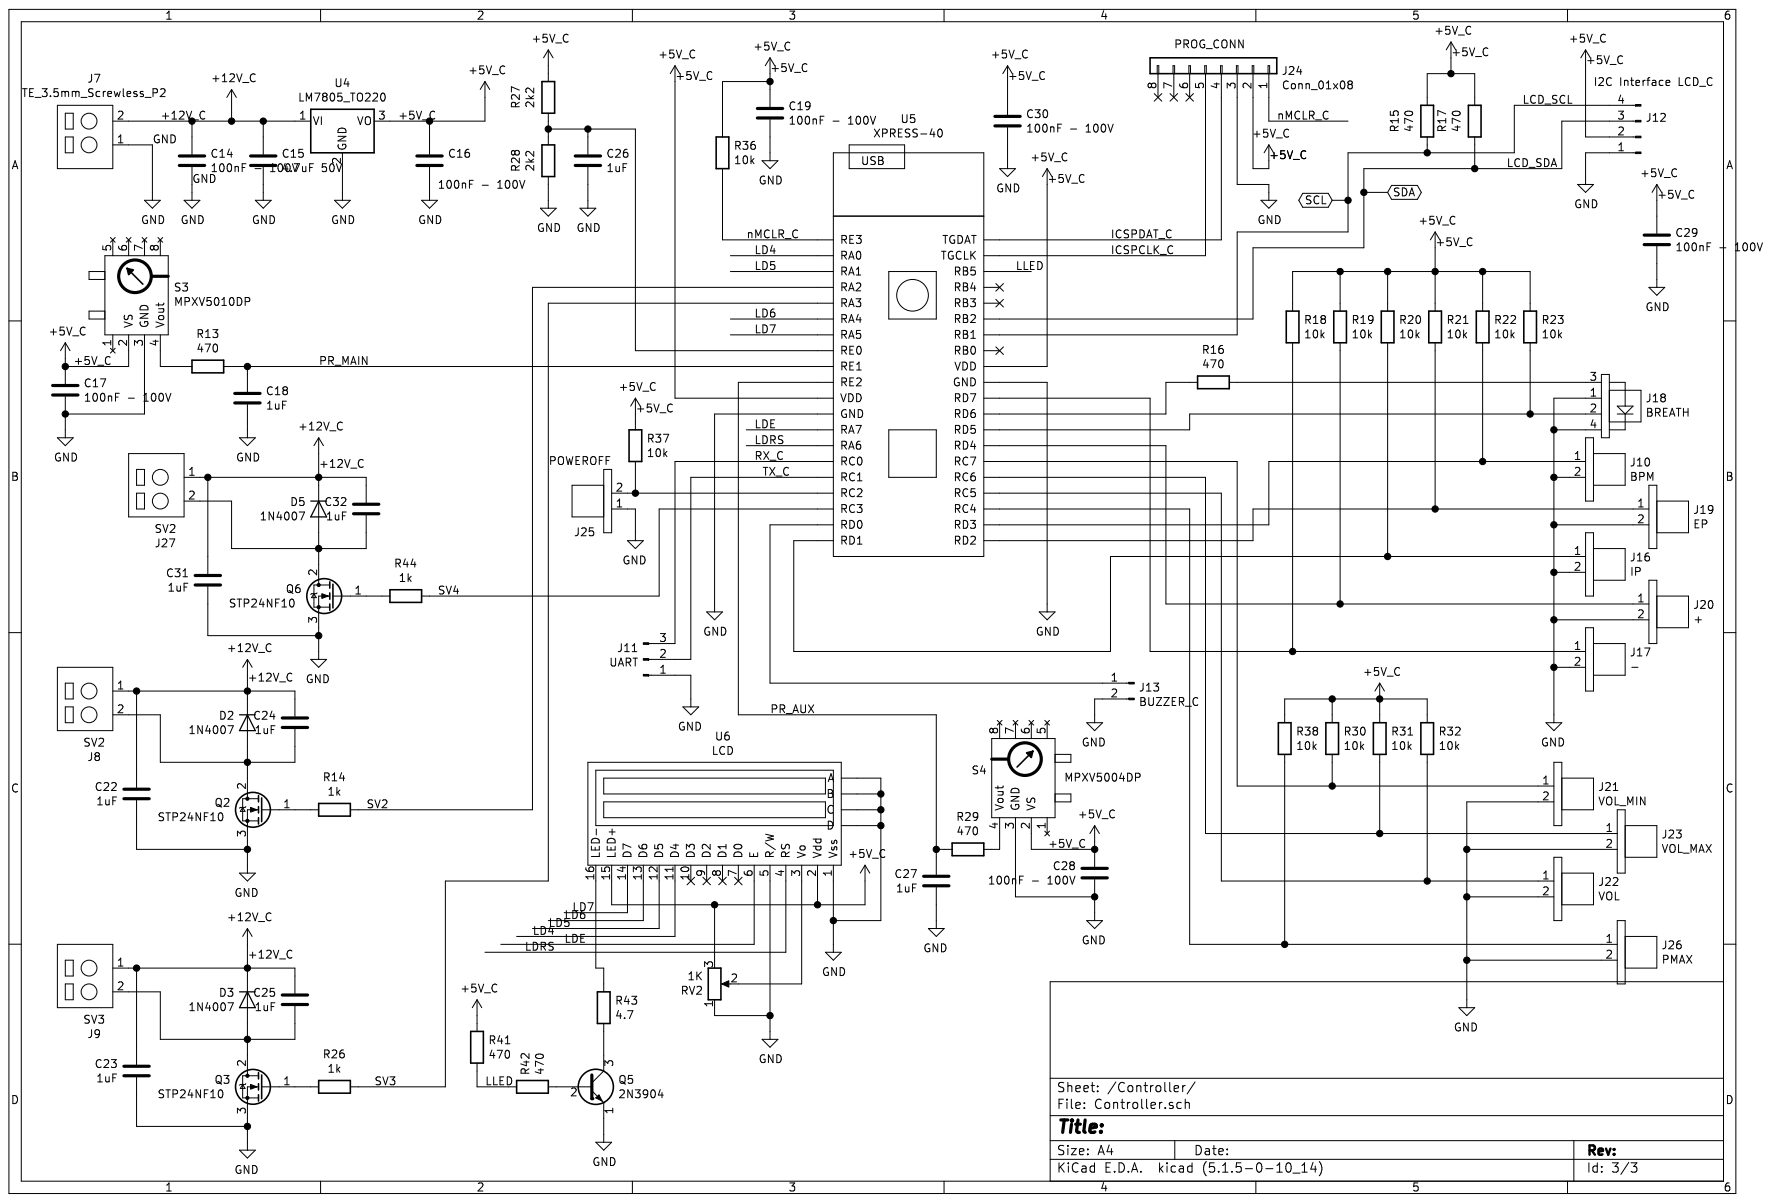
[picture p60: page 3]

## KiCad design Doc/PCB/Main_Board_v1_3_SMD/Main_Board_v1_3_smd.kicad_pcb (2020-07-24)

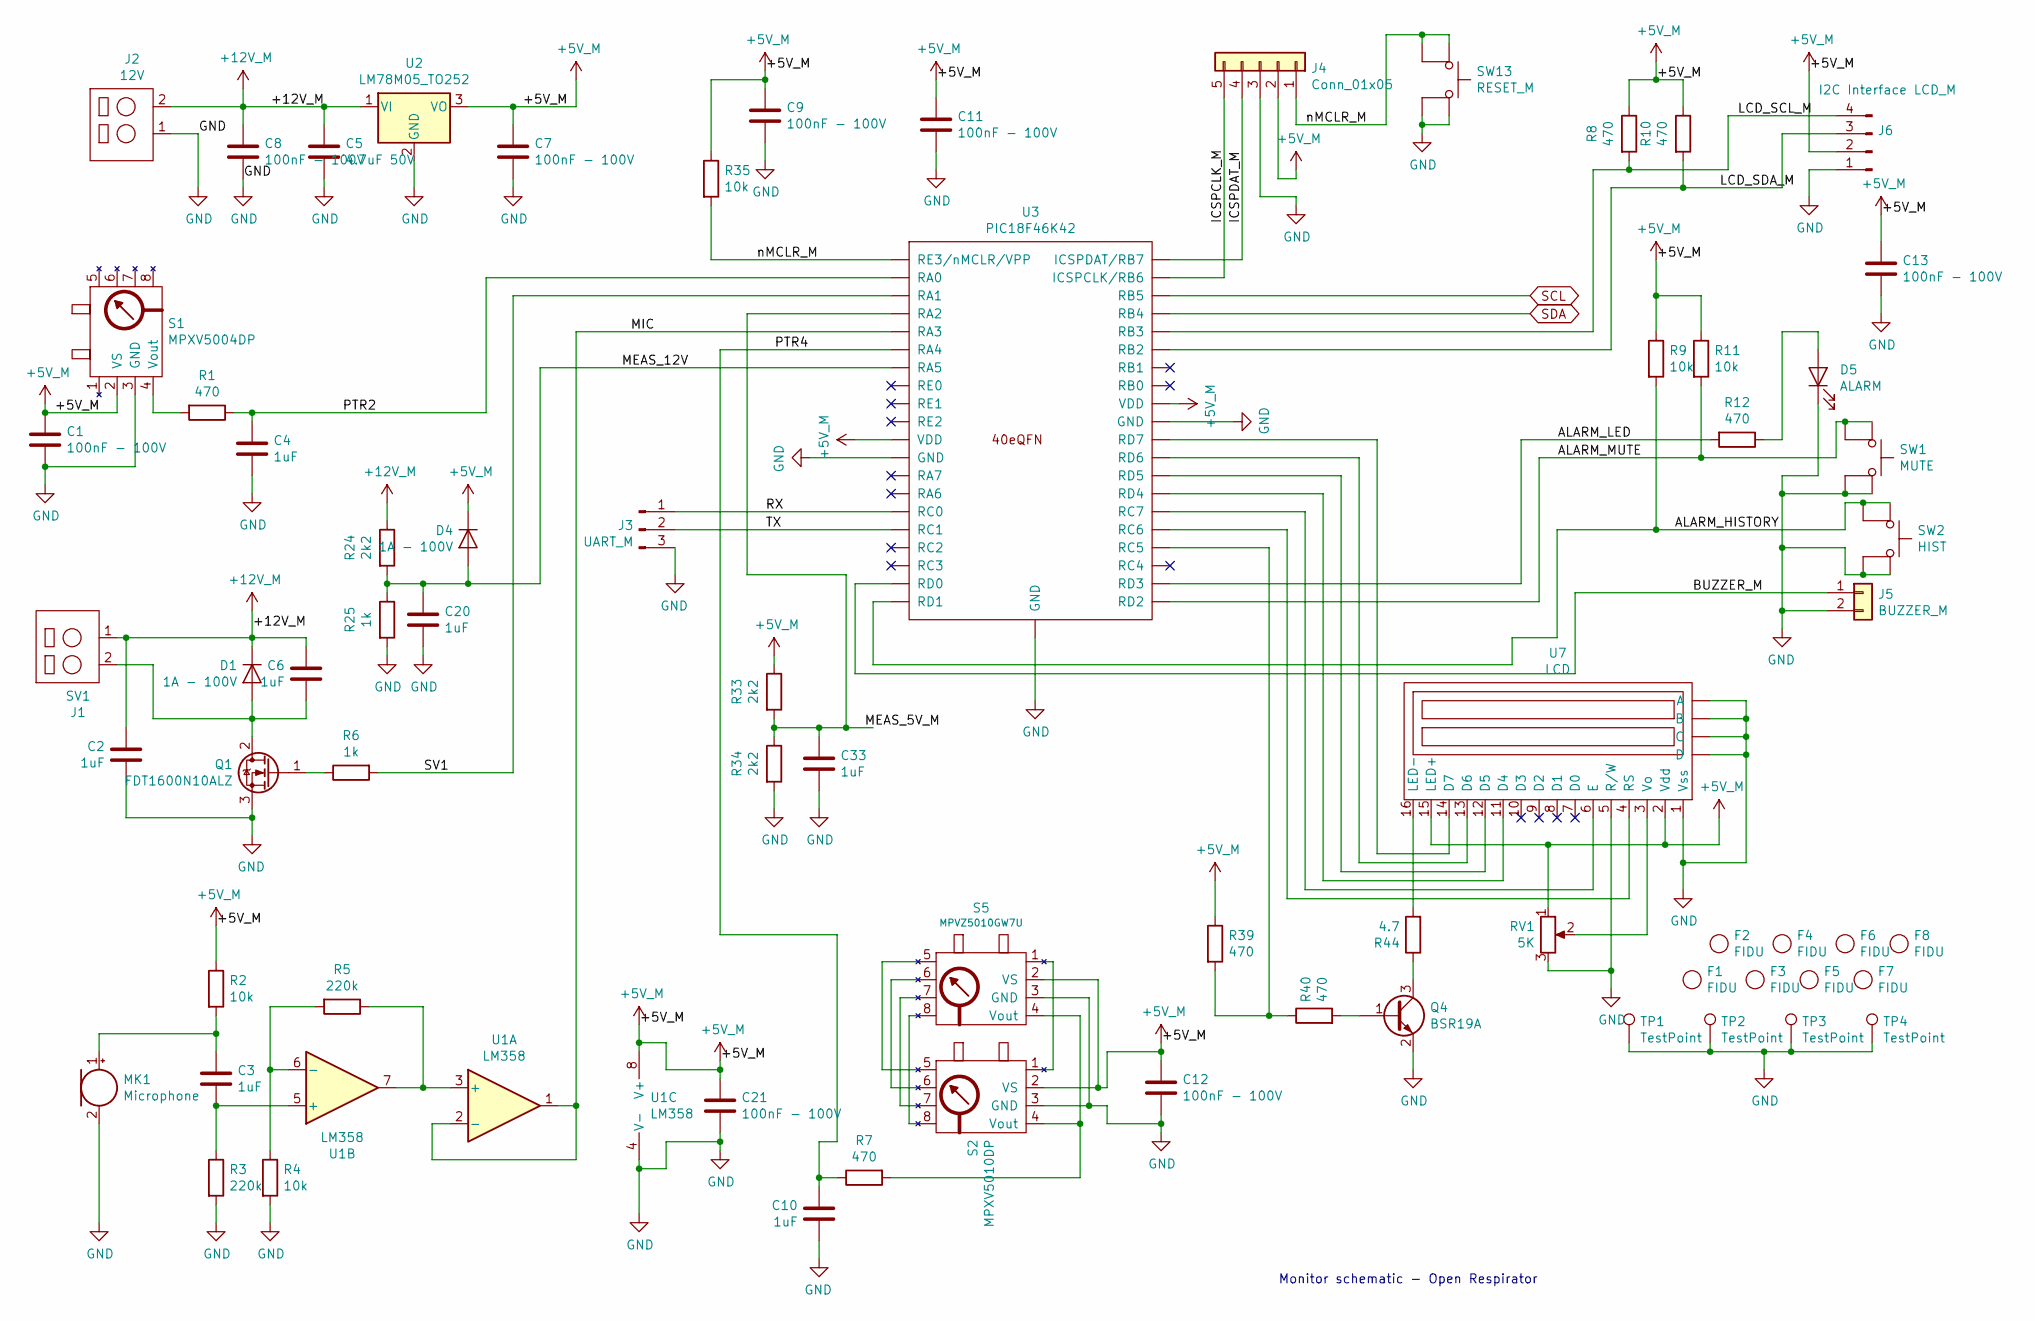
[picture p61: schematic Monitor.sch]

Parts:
C1, C7, C8, C9, C11, C12, C13, C21: 100nF - 100V; C_1206_3216Metric_Pad1.42x1.75mm_HandSolder
C2, C3, C4, C6, C10, C20, C33: 1uF; C_1206_3216Metric_Pad1.42x1.75mm_HandSolder
C5: 4.7uF 50V; CP_Radial_D5.0mm_P2.00mm
D1, D4: 1A - 100V; D_SMA-SMB_Universal_Handsoldering
D5: ALARM; LED_D3.0mm
F1, F2, F3, F4, F5, F6, F7, F8: FIDU; FIDUCIAL_TEST_PCB_1C
J1: SV1; PinHeader_1x02_Screwless_3.5mm
J2: 12V; PinHeader_1x02_Screwless_3.5mm
J3: UART_M; PinHeader_1x03_P2.54mm_Vertical
J4: Conn_01x05; PinHeader_1x05_P2.54mm_Horizontal
J5: BUZZER_M; PH_2_pol
J6: I2C Interface LCD_M; PH_4_pol
MK1: Microphone; MIC
Q1: FDT1600N10ALZ; SOT-223-3_TabPin2
Q4: BSR19A; SOT-23
R1, R7, R8, R10, R12, R39, R40: 470; R_0603_1608Metric_Pad1.05x0.95mm_HandSolder
R2, R4, R9, R11, R35: 10k; R_0603_1608Metric_Pad1.05x0.95mm_HandSolder
R3, R5: 220k; R_0603_1608Metric_Pad1.05x0.95mm_HandSolder
R6, R25: 1k; R_0603_1608Metric_Pad1.05x0.95mm_HandSolder
R24, R33, R34: 2k2; R_0603_1608Metric_Pad1.05x0.95mm_HandSolder
R44: 4.7; R_0603_1608Metric_Pad1.05x0.95mm_HandSolder
RV1: 5K; Potentiometer_Vishay_TS53YJ_Vertical
S1: MPXV5004DP; 1351-01
S2: MPXV5010DP; 1351-01
S5: MPVZ5010GW7U; 1560-03
SW1: MUTE; SW_PUSH_6mm_H13mm
SW2: HIST; SW_PUSH_6mm_H13mm
SW13: RESET_M; SW_PUSH_6mm_H13mm
TP1, TP2, TP3, TP4: TestPoint; PCB_DRILL
U1: LM358; SOIC-8-1EP_3.9x4.9mm_P1.27mm_EP2.41x3.3mm
U2: LM78M05_TO252; TO-252-2
U3: PIC18F46K42; QFN-40-1EP_5x5mm_P0.4mm_EP3.6x3.6mm_MedThermalVias
U7: LCD; LCD_2x16

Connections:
+5V_M: C1.1, C7.1, C9.1, C11.1, C12.1, C13.1, C21.1, D4.1 (K), J4.2, J6.2, R2.1, R8.1, R9.1, R10.1, R11.1, R33.1, R35.1, R39.1, RV1.1, S1.2 (VS), S2.2 (VS), S5.2 (VS), U1.8 (V+), U2.3 (VO), U3.7 (VDD), U3.26 (VDD), U7.2 (Vdd), U7.15 (LED+)
+12V_M: C2.1, C5.1, C6.1, C8.1, D1.1 (K), J1.1, J2.2, R24.1, U2.1 (VI)
/Monitor/ALARM_HISTORY: R9.2, SW2.1, U3.35 (RD1)
/Monitor/ALARM_LED: R12.2, U3.37 (RD3)
/Monitor/ALARM_MUTE: R11.2, SW1.1, U3.36 (RD2)
/Monitor/BUZZER_M: J5.1, U3.34 (RD0)
/Monitor/ICSPCLK_M: J4.5, U3.14 (ICSPCLK/RB6)
/Monitor/ICSPDAT_M: J4.4, U3.15 (ICSPDAT/RB7)
/Monitor/LCD_SCL_M: J6.4, R8.2, U3.11 (RB3)
/Monitor/LCD_SDA_M: J6.3, R10.2, U3.10 (RB2)
/Monitor/MEAS_5V_M: C33.1, R33.2, R34.1, U3.19 (RA2)
/Monitor/MEAS_12V: C20.1, D4.2 (A), R24.2, R25.1, U3.22 (RA5)
/Monitor/MIC: U1.1, U1.2 (-), U3.20 (RA3)
/Monitor/PTR2: C4.1, R1.1, U3.17 (RA0)
/Monitor/PTR4: C10.1, R7.1, U3.21 (RA4)
/Monitor/RX: J3.1, U3.30 (RC0)
/Monitor/SV1: R6.2, U3.18 (RA1)
/Monitor/TX: J3.2, U3.31 (RC1)
/Monitor/nMCLR_M: J4.1, R35.2, SW13.1, U3.16 (RE3/nMCLR/VPP)
GND: C1.2, C2.2, C4.2, C5.2, C7.2, C8.2, C9.2, C10.2, C11.2, C12.2, C13.2, C20.2, C21.2, C33.2, D5.1 (K), J2.1, J3.3, J4.3, J5.2, J6.1, MK1.2 (-), Q1.3 (S), Q4.2 (E), R3.2, R4.2, R25.2, R34.2, RV1.3, S1.3 (GND), S2.3 (GND), S5.3 (GND), SW1.2, SW2.2, SW13.2, TP1.1, TP2.1, TP3.1, TP4.1, U1.4 (V-), U2.2 (GND), U3.6 (GND), U3.27 (GND), U3.41 (GND), U7.1 (Vss), U7.5 (R/W), U7.~ (A); also elsewhere on the board
unnamed: C3.1, MK1.1 (+), R2.2
unnamed: C3.2, R3.1, U1.5 (+)
unnamed: C6.2, D1.2 (A), J1.2, Q1.2 (D)
unnamed: D5.2 (A), R12.1
unnamed: Q1.1 (G), R6.1
unnamed: Q4.1 (B), R40.2
unnamed: Q4.3 (C), R44.1
unnamed: R1.2, S1.4 (Vout)
unnamed: R4.1, R5.2, U1.6 (-)
unnamed: R5.1, U1.3 (+), U1.7
unnamed: R7.2, S2.4 (Vout), S5.4 (Vout)
unnamed: R39.2, R40.1, U3.39 (RC5)
unnamed: R44.2, U7.16 (LED-)
unnamed: RV1.2, U7.3 (Vo)
unnamed: S2.1, S5.1
unnamed: S2.5, S5.5
unnamed: S2.6, S5.6
unnamed: S2.7, S5.7
unnamed: S2.8, S5.8
unnamed: U3.1 (RC7), U7.6 (E)
unnamed: U3.2 (RD4), U7.11 (D4)
unnamed: U3.3 (RD5), U7.12 (D5)
unnamed: U3.4 (RD6), U7.13 (D6)
unnamed: U3.5 (RD7), U7.14 (D7)
unnamed: U3.40 (RC6), U7.4 (RS)
SCL: U3.13 (RB5); also elsewhere on the board
SDA: U3.12 (RB4); also elsewhere on the board

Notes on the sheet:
Monitor schematic - Open Respirator

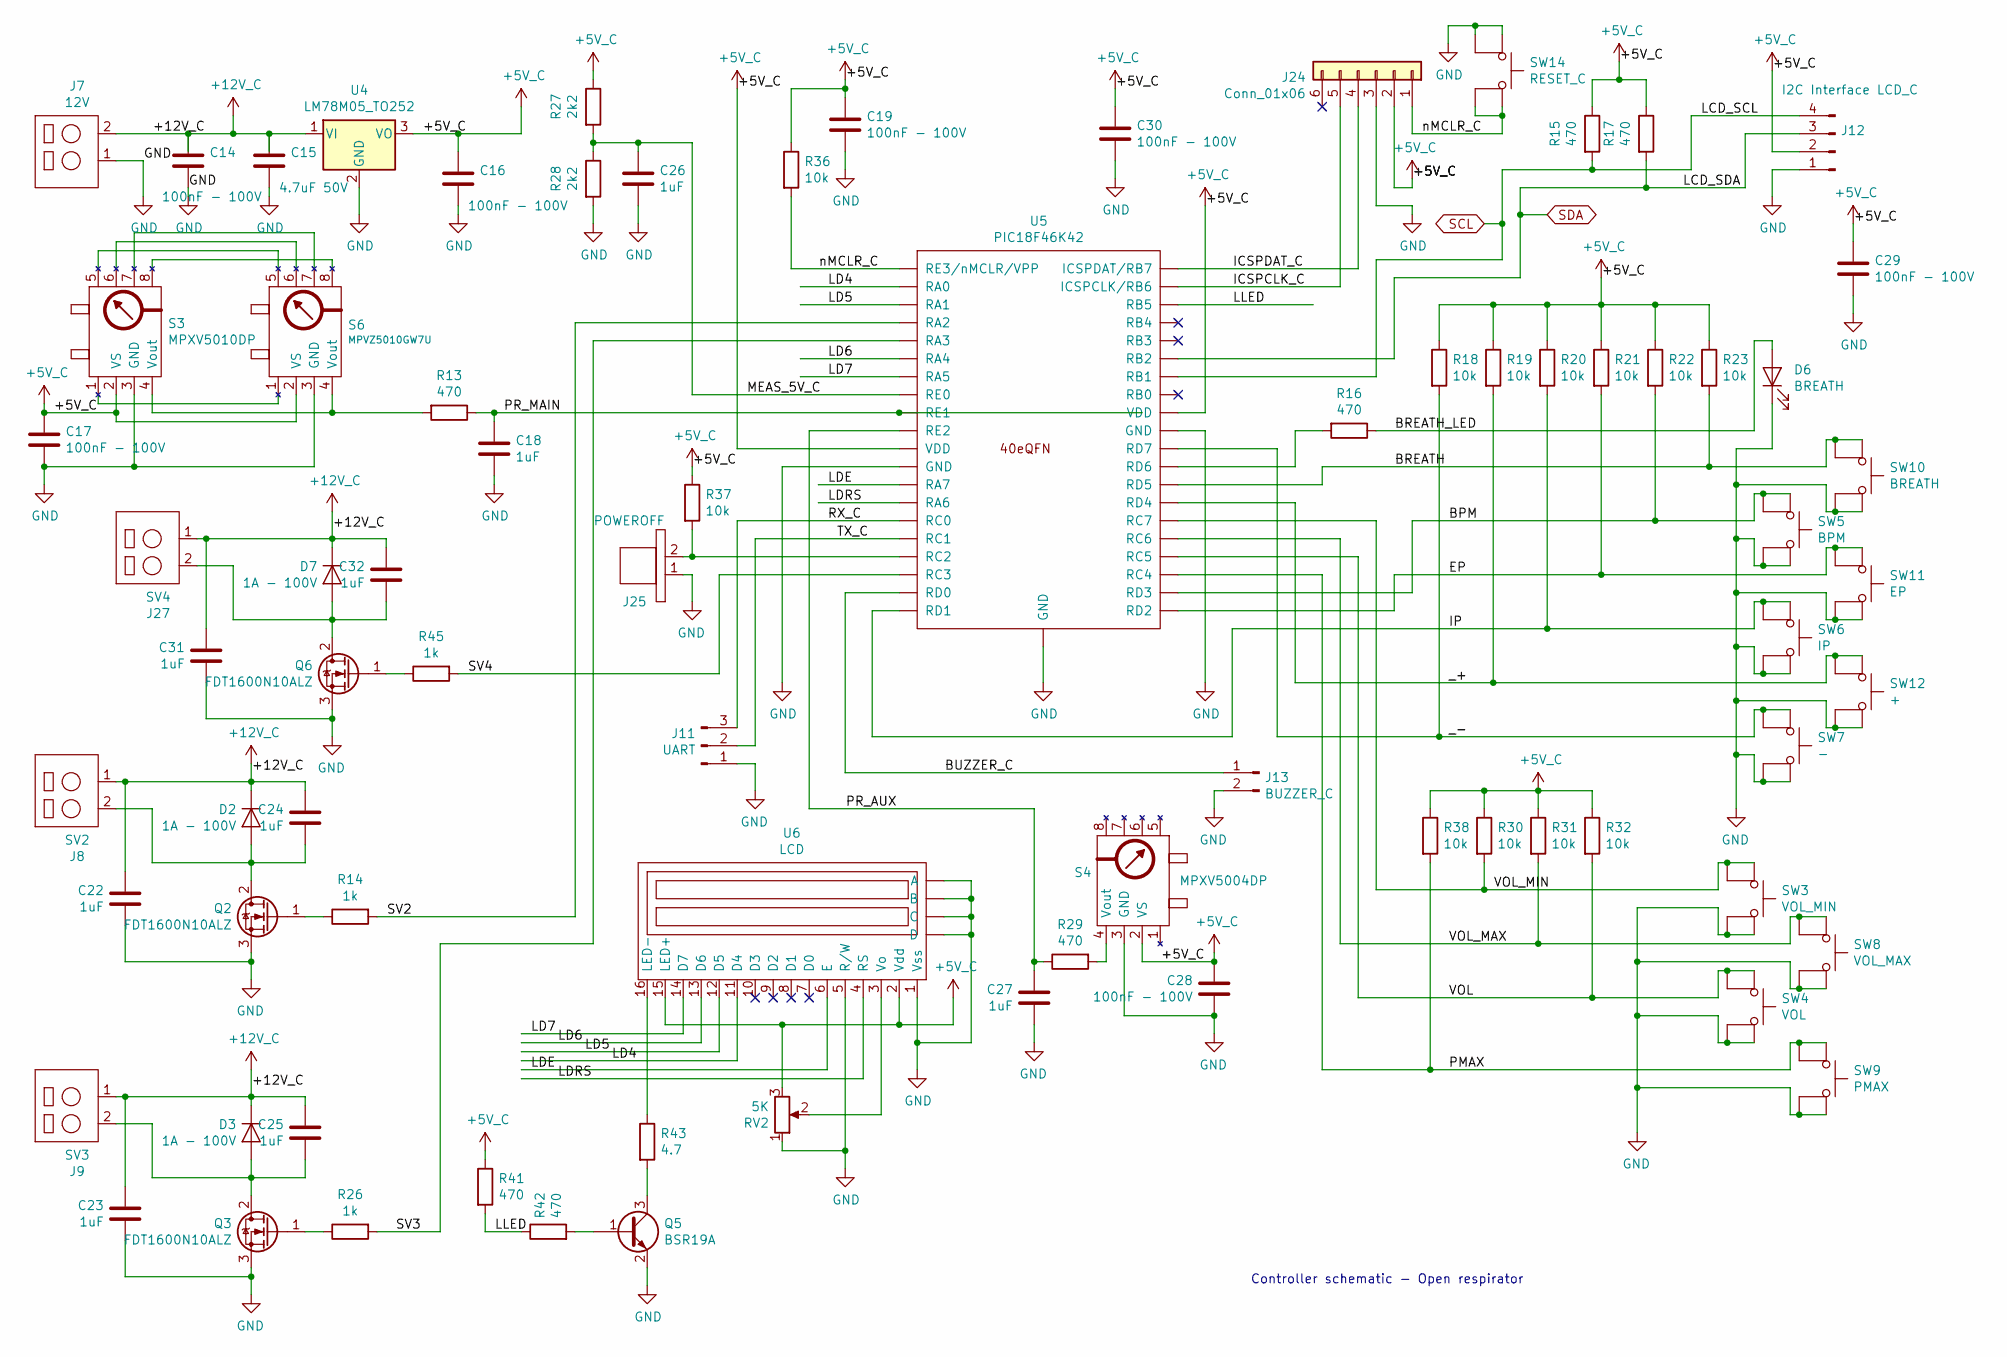
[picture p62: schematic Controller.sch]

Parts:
C14, C16, C17, C19, C28, C29, C30: 100nF - 100V; C_1206_3216Metric_Pad1.42x1.75mm_HandSolder
C15: 4.7uF 50V; CP_Radial_D5.0mm_P2.00mm
C18, C22, C23, C24, C25, C26, C27, C31, C32: 1uF; C_1206_3216Metric_Pad1.42x1.75mm_HandSolder
D2, D3, D7: 1A - 100V; D_SMA-SMB_Universal_Handsoldering
D6: BREATH; LED_D3.0mm
J7: 12V; PinHeader_1x02_Screwless_3.5mm
J8: SV2; PinHeader_1x02_Screwless_3.5mm
J9: SV3; PinHeader_1x02_Screwless_3.5mm
J11: UART; PinHeader_1x03_P2.54mm_Vertical
J12: I2C Interface LCD_C; PH_4_pol
J13: BUZZER_C; PinHeader_1x02_P2.54mm_Vertical
J24: Conn_01x06; PinHeader_1x06_P2.54mm_Horizontal
J25: POWEROFF; PH_2_pol
J27: SV4; PinHeader_1x02_Screwless_3.5mm
Q2, Q3, Q6: FDT1600N10ALZ; SOT-223-3_TabPin2
Q5: BSR19A; SOT-23
R13, R15, R16, R17, R29, R41, R42: 470; R_0603_1608Metric_Pad1.05x0.95mm_HandSolder
R14, R26, R45: 1k; R_0603_1608Metric_Pad1.05x0.95mm_HandSolder
R18, R19, R20, R21, R22, R23, R30, R31, R32, R36, R37, R38: 10k; R_0603_1608Metric_Pad1.05x0.95mm_HandSolder
R27, R28: 2k2; R_0603_1608Metric_Pad1.05x0.95mm_HandSolder
R43: 4.7; R_0603_1608Metric_Pad1.05x0.95mm_HandSolder
RV2: 5K; Potentiometer_Vishay_TS53YJ_Vertical
S3: MPXV5010DP; 1351-01
S4: MPXV5004DP; 1351-01
S6: MPVZ5010GW7U; 1560-03
SW3: VOL_MIN; SW_PUSH_6mm_H13mm
SW4: VOL; SW_PUSH_6mm_H13mm
SW5: BPM; SW_PUSH_6mm_H13mm
SW6: IP; SW_PUSH_6mm_H13mm
SW7: -; SW_PUSH_6mm_H13mm
SW8: VOL_MAX; SW_PUSH_6mm_H13mm
SW9: PMAX; SW_PUSH_6mm_H13mm
SW10: BREATH; SW_PUSH_6mm_H13mm
SW11: EP; SW_PUSH_6mm_H13mm
SW12: +; SW_PUSH_6mm_H13mm
SW14: RESET_C; SW_PUSH_6mm_H13mm
U4: LM78M05_TO252; TO-252-2
U5: PIC18F46K42; QFN-40-1EP_5x5mm_P0.4mm_EP3.6x3.6mm_MedThermalVias
U6: LCD; LCD_2x16

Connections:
+5V_C: C16.1, C17.1, C19.1, C28.1, C29.1, C30.1, J12.2, J24.2, R15.1, R17.1, R18.1, R19.1, R20.1, R21.1, R22.1, R23.1, R27.1, R30.1, R31.1, R32.1, R36.1, R37.1, R38.1, R41.1, RV2.3, S3.2 (VS), S4.2 (VS), S6.2 (VS), U4.3 (VO), U5.7 (VDD), U5.26 (VDD), U6.2 (Vdd), U6.15 (LED+)
+12V_C: C14.1, C15.1, C22.1, C23.1, C24.1, C25.1, C31.1, C32.1, D2.1 (K), D3.1 (K), D7.1 (K), J7.2, J8.1, J9.1, J27.1, U4.1 (VI)
/Controller/BPM: R22.2, SW5.1, U5.37 (RD3)
/Controller/BREATH: R23.2, SW10.1, U5.3 (RD5)
/Controller/BREATH_LED: D6.2 (A), R16.1
/Controller/BUZZER_C: J13.1, U5.34 (RD0)
/Controller/EP: R21.2, SW11.1, U5.36 (RD2)
/Controller/ICSPCLK_C: J24.5, U5.14 (ICSPCLK/RB6)
/Controller/ICSPDAT_C: J24.4, U5.15 (ICSPDAT/RB7)
/Controller/IP: R20.2, SW6.1, U5.35 (RD1)
/Controller/LD4: U5.17 (RA0), U6.11 (D4)
/Controller/LD5: U5.18 (RA1), U6.12 (D5)
/Controller/LD6: U5.21 (RA4), U6.13 (D6)
/Controller/LD7: U5.22 (RA5), U6.14 (D7)
/Controller/LDE: U5.28 (RA7), U6.6 (E)
/Controller/LDRS: U5.29 (RA6), U6.4 (RS)
/Controller/LLED: R41.2, R42.1, U5.13 (RB5)
/Controller/MEAS_5V_C: C26.1, R27.2, R28.1, U5.23 (RE0)
/Controller/PMAX: R38.2, SW9.1, U5.38 (RC4)
/Controller/PR_AUX: C27.1, R29.1, U5.25 (RE2)
/Controller/PR_MAIN: C18.1, R13.1, U5.24 (RE1)
/Controller/RX_C: J11.3, U5.30 (RC0)
/Controller/SV2: R14.2, U5.19 (RA2)
/Controller/SV3: R26.2, U5.20 (RA3)
/Controller/SV4: R45.2, U5.33 (RC3)
/Controller/TX_C: J11.2, U5.31 (RC1)
/Controller/VOL: R32.2, SW4.1, U5.39 (RC5)
/Controller/VOL_MAX: R31.2, SW8.1, U5.40 (RC6)
/Controller/VOL_MIN: R30.2, SW3.1, U5.1 (RC7)
/Controller/_+: R19.2, SW12.1, U5.2 (RD4)
/Controller/_-: R18.2, SW7.1, U5.5 (RD7)
/Controller/nMCLR_C: J24.1, R36.2, SW14.2, U5.16 (RE3/nMCLR/VPP)
GND: C14.2, C15.2, C16.2, C17.2, C18.2, C19.2, C22.2, C23.2, C26.2, C27.2, C28.2, C29.2, C30.2, C31.2, D6.1 (K), J7.1, J11.1, J12.1, J13.2, J24.3, J25.1, Q2.3 (S), Q3.3 (S), Q5.2 (E), Q6.3 (S), R28.2, RV2.1, S3.3 (GND), S4.3 (GND), S6.3 (GND), SW3.2, SW4.2, SW5.2, SW6.2, SW7.2, SW8.2, SW9.2, SW10.2, SW11.2, SW12.2, SW14.1, U4.2 (GND), U5.6 (GND), U5.27 (GND), U5.41 (GND), U6.1 (Vss), U6.5 (R/W), U6.~ (A); also elsewhere on the board
unnamed: C24.2, D2.2 (A), J8.2, Q2.2 (D)
unnamed: C25.2, D3.2 (A), J9.2, Q3.2 (D)
unnamed: C32.2, D7.2 (A), J27.2, Q6.2 (D)
unnamed: J25.2, R37.2, U5.32 (RC2)
unnamed: Q2.1 (G), R14.1
unnamed: Q3.1 (G), R26.1
unnamed: Q5.1 (B), R42.2
unnamed: Q5.3 (C), R43.2
unnamed: Q6.1 (G), R45.1
unnamed: R13.2, S3.4 (Vout), S6.4 (Vout)
unnamed: R16.2, U5.4 (RD6)
unnamed: R29.2, S4.4 (Vout)
unnamed: R43.1, U6.16 (LED-)
unnamed: RV2.2, U6.3 (Vo)
unnamed: S3.1, S6.1
unnamed: S3.5, S6.5
unnamed: S3.6, S6.6
unnamed: S3.7, S6.7
unnamed: S3.8, S6.8
SCL: J12.4, R15.2, U5.9 (RB1); also elsewhere on the board
SDA: J12.3, R17.2, U5.10 (RB2); also elsewhere on the board

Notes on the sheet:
Controller schematic - Open respirator

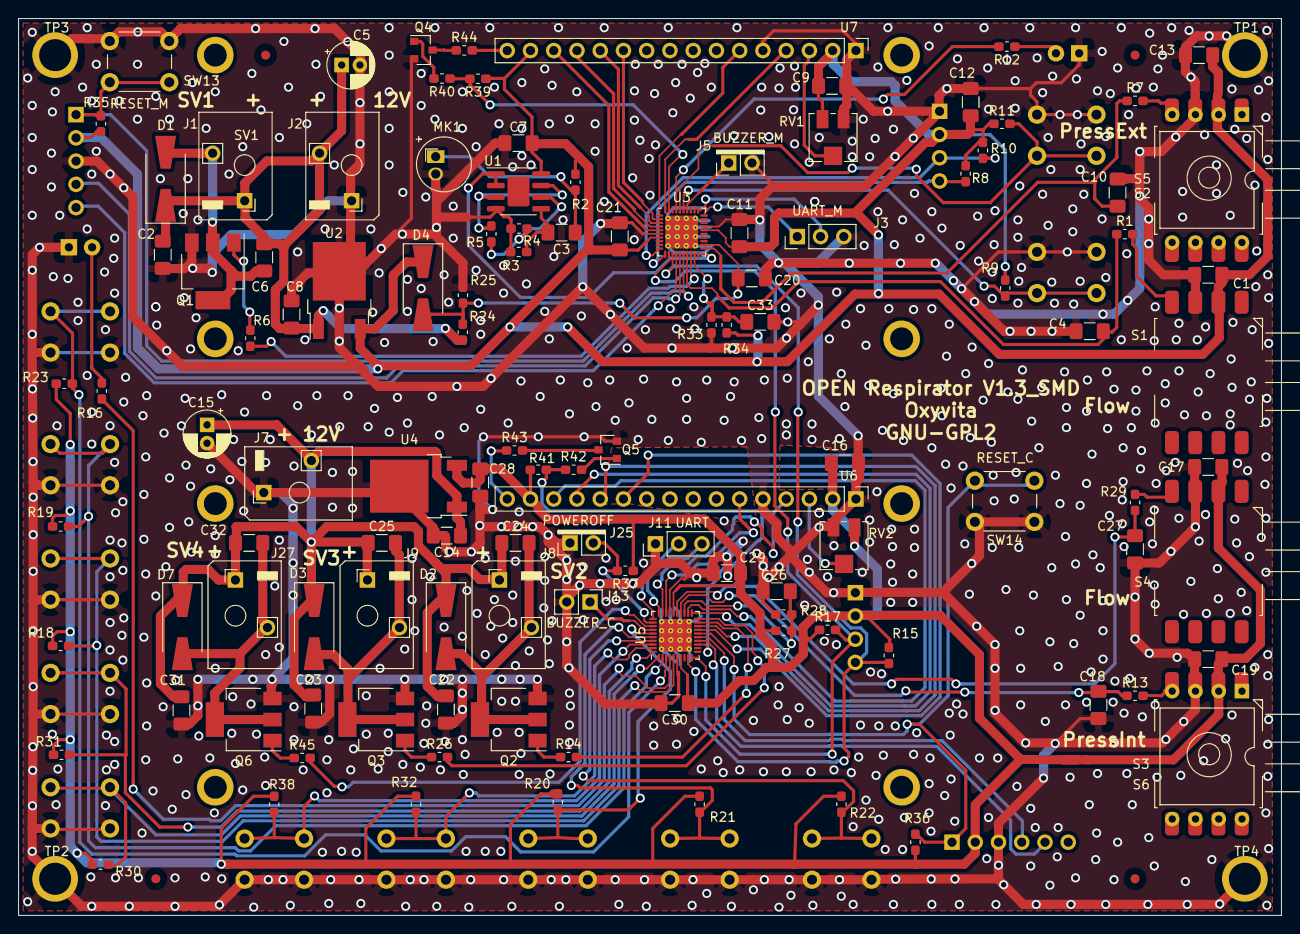
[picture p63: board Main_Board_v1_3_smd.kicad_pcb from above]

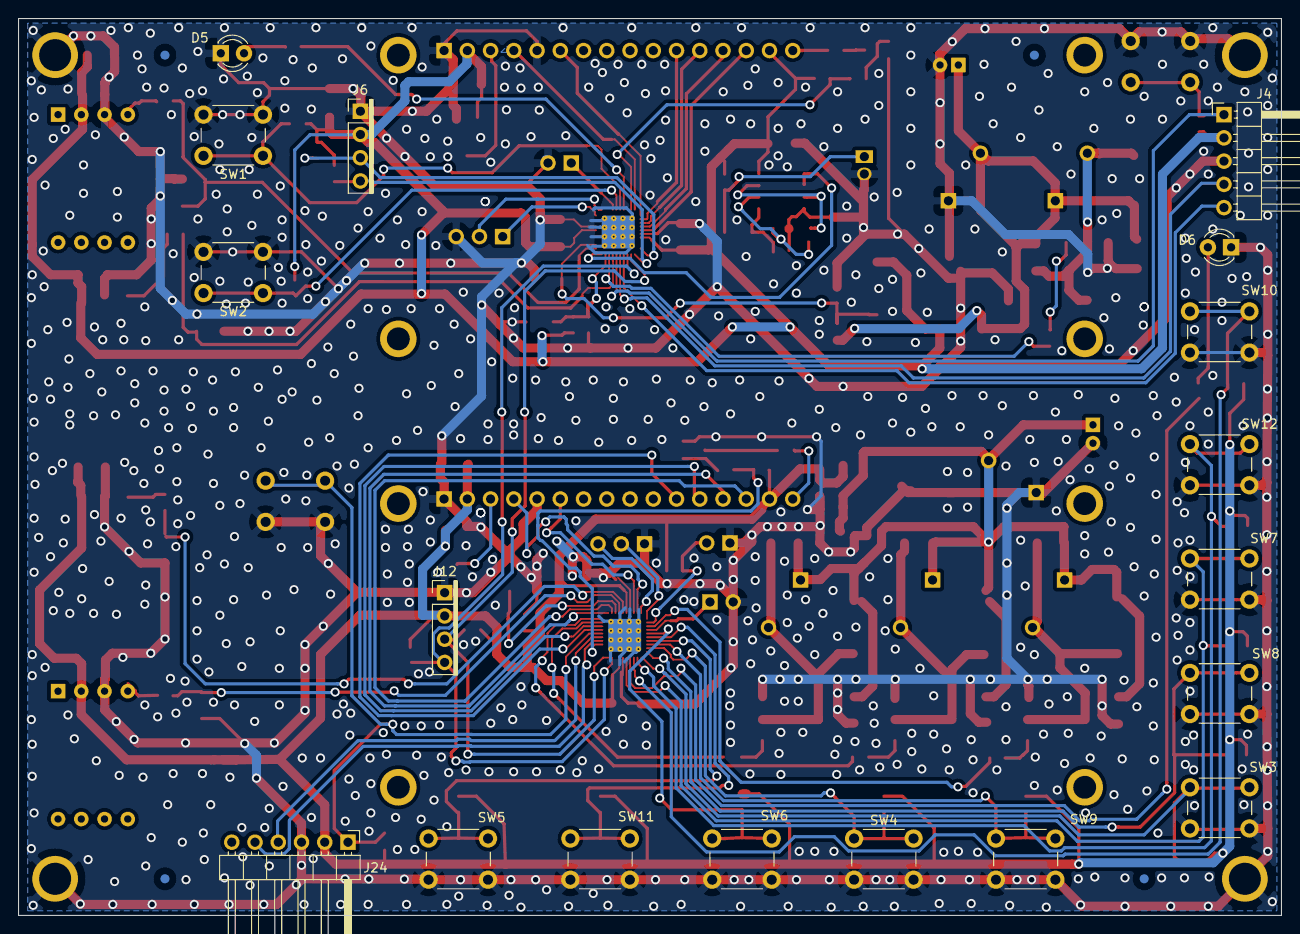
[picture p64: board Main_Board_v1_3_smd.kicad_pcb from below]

Board: 2 copper layers, 138.0 x 98.0 mm, 148 parts (22 on the bottom side), 98 nets.

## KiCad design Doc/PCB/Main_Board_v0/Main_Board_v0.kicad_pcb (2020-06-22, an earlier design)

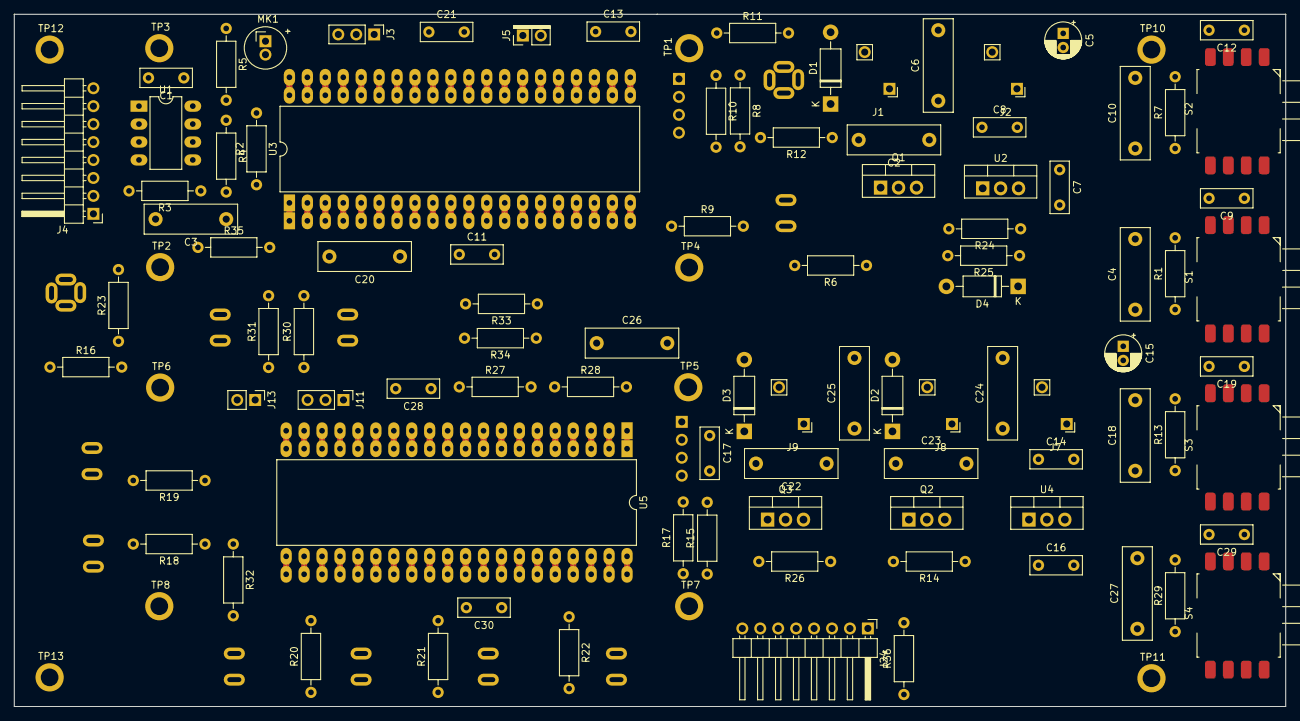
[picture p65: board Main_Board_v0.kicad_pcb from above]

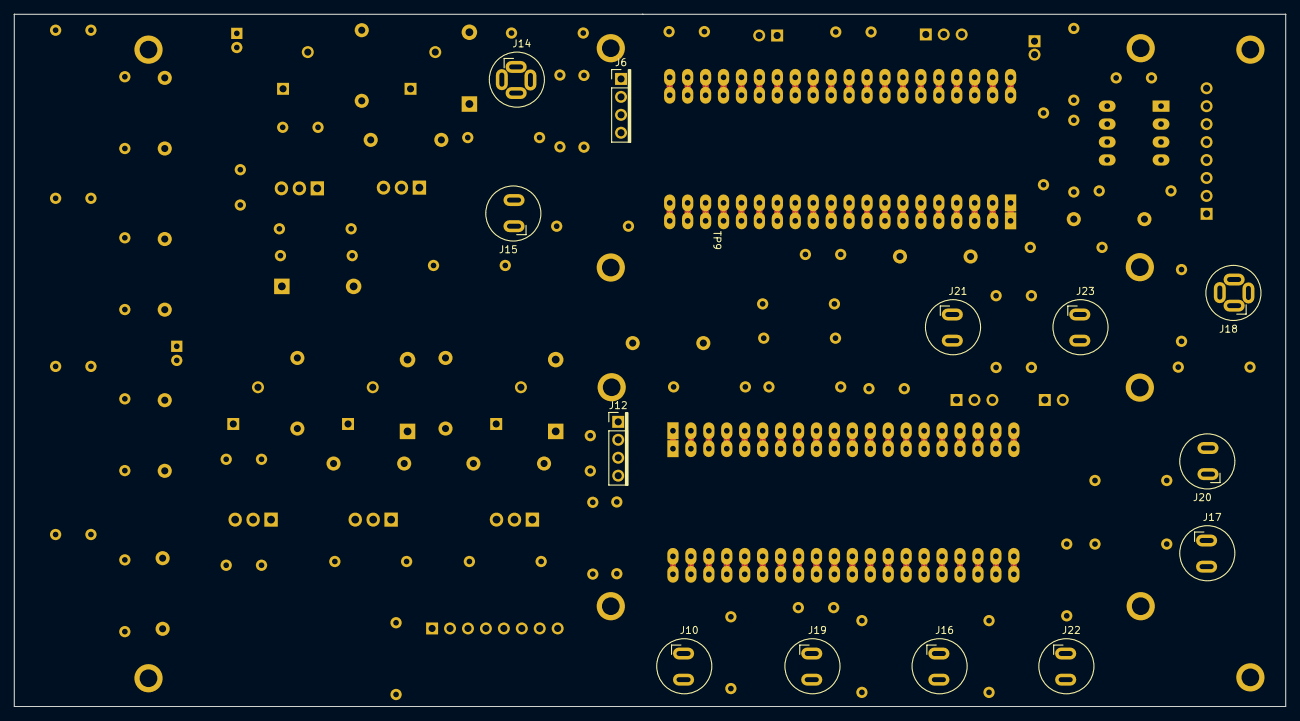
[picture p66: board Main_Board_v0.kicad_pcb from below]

Board: 2 copper layers, 180.0 x 98.0 mm, 120 parts (14 on the bottom side), 62 nets, no tracks yet.

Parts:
C1, C7, C8, C9, C11, C12, C13, C14, C16, C17, C19, C21, C28, C29, C30: 100nF - 100V; C_Rect_L7.2mm_W2.5mm_P5.00mm_FKS2_FKP2_MKS2_MKP2
C2, C3, C4, C6, C10, C18, C20, C22, C23, C24, C25, C26, C27: 1uF; C_Rect_L13.0mm_W4.0mm_P10.00mm_FKS3_FKP3_MKS4
C5, C15: 4.7uF 50V; CP_Radial_D5.0mm_P2.00mm
D1, D2, D3, D4: 1N4007; D_DO-41_SOD81_P10.16mm_Horizontal
J1, J2, J7: TE_3.5mm_Screwless_P2; PinHeader_1x02_Screwless_3.5mm
J3: UART_M; PinHeader_1x03_P2.54mm_Vertical
J4, J24: Conn_01x08; PinHeader_1x08_P2.54mm_Horizontal
J5: BUZZER; PH_2_pol
J6: I2C Interface LCD_M; PH_4_pol
J8: SV2; PinHeader_1x02_Screwless_3.5mm
J9: SV3; PinHeader_1x02_Screwless_3.5mm
J10: BPM; PushButton
J11: UART; PinHeader_1x03_P2.54mm_Vertical
J12: I2C Interface LCD_C; PH_4_pol
J13: BUZZER_C; PinHeader_1x02_P2.54mm_Vertical
J14: Button_LED; PushButton_LED
J15: Button; PushButton
J16: IP; PushButton
J17: -; PushButton
J18: BREATH; PushButton_LED
J19: EP; PushButton
J20: +; PushButton
J21: VOL_MIN; PushButton
J22: VOL; PushButton
J23: VOL_MAX; PushButton
MK1: Microphone; MIC
Q1, Q2, Q3: IRLZ34N; TO-220-3_Vertical
R1, R7, R8, R10, R12, R13, R15, R16, R17, R29, R33, R34: 470; R_Axial_DIN0207_L6.3mm_D2.5mm_P10.16mm_Horizontal
R2, R4, R9, R11, R18, R19, R20, R21, R22, R23, R25, R27, R28, R30, R31, R32, R35, R36: 10k; R_Axial_DIN0207_L6.3mm_D2.5mm_P10.16mm_Horizontal
R3, R5: 220k; R_Axial_DIN0207_L6.3mm_D2.5mm_P10.16mm_Horizontal
R6, R14, R26: 50; R_Axial_DIN0207_L6.3mm_D2.5mm_P10.16mm_Horizontal
R24: 22k; R_Axial_DIN0207_L6.3mm_D2.5mm_P10.16mm_Horizontal
S1, S2, S3, S4: MPXV5004DP; 1351-01
TP1, TP2, TP3, TP4, TP5, TP6, TP7, TP8, TP10, TP11, TP12, TP13: TestPoint; LCD_DRILL
TP9: TestPoint_Alt; pcb
U1: LM358; DIP-8_W7.62mm_LongPads
U2, U4: LM7805_TO220; TO-220-3_Vertical
U3, U5: XPRESS-40; EXPRESS-40_DIP_40

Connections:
+5V_C: C16.1, C17.1, C19.1, C28.1, C29.1, C30.1, J12.2, J24.2, R15.1, R17.1, R18.1, R19.1, R20.1, R21.1, R22.1, R23.1, R27.1, R30.1, R31.1, R32.1, R36.1, S3.2, S4.2, U4.3, U5.11, U5.32
+5V_M: C1.1, C7.1, C9.1, C11.1, C12.1, C13.1, C21.1, D4.1, J4.2, J6.2, R2.1, R8.1, R9.1, R10.1, R11.1, R33.1, R34.1, R35.1, S1.2, S2.2, U1.8, U2.3, U3.11, U3.32
+12V_C: C14.1, C15.1, C22.1, C23.1, C24.1, C25.1, D2.1, D3.1, J7.2, J8.1, J9.1, U4.1
+12V_M: C2.1, C5.1, C6.1, C8.1, D1.1, J1.1, J2.2, R24.1, U2.1
/Controller/ICSPCLK_C: J24.5, U5.39
/Controller/ICSPDAT_C: J24.4, U5.40
/Controller/LCD_SCL: J12.4, R15.2, U5.38
/Controller/LCD_SDA: J12.3, R17.2, U5.37
/Controller/PR2: C18.1, R13.1, U5.2
/Controller/PR3: C27.1, R29.1, U5.5
/Controller/SV2: R14.2, U5.3
/Controller/SV3: R26.2, U5.4
/Controller/nMCLR_C: J24.1, R36.2, U5.1
/Monitor/ALARM_HISTORY: J15.1, R9.2, U3.28
/Monitor/ALARM_LED: R12.2, U3.30
/Monitor/ALARM_MUTE: J14.1, R11.2, U3.29
/Monitor/BUZZER: J5.1, U3.27
/Monitor/ICSPCLK_M: J4.5, U3.39
/Monitor/ICSPDAT_M: J4.4, U3.40
/Monitor/LCD_SCL_M: J6.4, R8.2, U3.36
/Monitor/LCD_SDA_M: J6.3, R10.2, U3.35
/Monitor/MEAS_12V: C20.1, D4.2, R24.2, R25.1, U3.7
/Monitor/MIC: U1.1, U1.2, U3.5
/Monitor/PTR2: C4.1, R1.1, U3.2
/Monitor/PTR4: C10.1, R7.1, U3.6
/Monitor/RX: J3.1, U3.15
/Monitor/SV1: R6.2, U3.3
/Monitor/TX: J3.2, U3.16
/Monitor/nMCLR_M: J4.1, R35.2, U3.1
GND: C1.2, C2.2, C4.2, C5.2, C7.2, C8.2, C9.2, C10.2, C11.2, C12.2, C13.2, C14.2, C15.2, C16.2, C17.2, C18.2, C19.2, C20.2, C21.2, C22.2, C23.2, C26.2, C27.2, C28.2, C29.2, C30.2, J2.1, J3.3, J4.3, J5.2, J6.1, J7.1, J10.2, J11.1, J12.1, J13.2, J14.2, J14.4, J15.2, J16.2, J17.2, J18.1, J18.4, J19.2, J20.2, J21.2, J22.2, J23.2, J24.3, MK1.1, Q1.3, Q2.3, Q3.3, R3.2, R4.2, R25.2, R28.2, S1.3, S2.3, S3.3, S4.3, TP1.1, TP2.1, TP3.1, TP4.1, TP5.1, TP6.1, TP7.1, TP8.1, TP10.1, TP11.1, TP12.1, TP13.1, U1.4, U2.2, U3.12, U3.31, U4.2, U5.12, U5.31
unnamed: C3.1, MK1.2, R2.2
unnamed: C3.2, R3.1, U1.5
unnamed: C6.2, D1.2, J1.2, Q1.2
unnamed: C24.2, D2.2, J8.2, Q2.2
unnamed: C25.2, D3.2, J9.2, Q3.2
unnamed: C26.1, R27.2, R28.1, U5.6
unnamed: J10.1, R22.2, U5.28
unnamed: J11.2, U5.15
unnamed: J11.3, U5.16
unnamed: J13.1, U5.19
unnamed: J14.3, R12.1
unnamed: J16.1, R20.2, U5.22
unnamed: J17.1, R18.2, U5.20
unnamed: J18.2, R23.2, U5.29
unnamed: J18.3, R16.1
unnamed: J19.1, R21.2, U5.27
unnamed: J20.1, R19.2, U5.21
unnamed: J21.1, R30.2, U5.26
unnamed: J22.1, R32.2, U5.24
unnamed: J23.1, R31.2, U5.25
unnamed: Q1.1, R6.1
unnamed: Q2.1, R14.1
unnamed: Q3.1, R26.1
unnamed: R1.2, S1.4
unnamed: R4.1, R5.2, U1.6
unnamed: R5.1, U1.3, U1.7
unnamed: R7.2, S2.4
unnamed: R13.2, S3.4
unnamed: R16.2, U5.30
unnamed: R29.2, S4.4
SCL: R33.2, U3.38, U5.18
SDA: R34.2, U3.37, U5.23

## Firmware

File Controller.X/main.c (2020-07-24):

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
// Author: David Ortiz
//  This file is part of project: OpenRespirator
//

#include "mcc_generated_files/mcc.h"
#include "ORespGlobal.h"
#include "aCapture.h"
#include "time.h"
#include "cmath.h"
#include "vMeasure.h"
#include "keyRead.h"
#include "LiquidCrystal_I2C.h"
#include "menu.h"
#include "brate.h"
#include "selftest.h"
#include "monComm.h"
#include "i2c2_mux.h"

#ifdef DEBUG

#define DBGPCONVERT(pValue) ((int16_t) (((2560/MPRESSURE_MBAR(1))*((int24_t) pValue))>>8))

void putch(char byte) {
    while (!UART1_is_tx_ready());
    UART1_Write(byte);
}
#endif

// To avoid problems with control, keep a copy of the values during first part of inspiration and expiration.
int16_t intBdTrig, intIP, intMaxP, intPEEP, intIDuration, intEDuration, intMaxV;
vmodeT intVentMode; 

///////////////////
// User parameters.
///////////////////
vmodeT   VentMode = 1; // 0 --> Pressure-control, 1 --> Volume-control.
uint8_t  MaxP = 40;
// Volume is in units of 10ml.
uint8_t  MaxV = 40;
uint8_t  LowVAlarm = 34;
uint8_t  HighVAlarm = 46;
uint8_t BPM = 20;
uint16_t IDuration, EDuration;
uint8_t IP = 30;
uint8_t PEEP = 15;
uint8_t BdTrig = 2;
bool    sBreath;

// CONTROLLER INTERNAL PARAMETERS.
#define BLED_ONTIME TIME_MS(500)
// DO NOT CHANGE. NEEDED TO ENSURE STABILITY.
#define PEEPCTRLMIN   MPRESSURE_MBAR(1)

#define PIPLATEAUMDEL TIME_MS(150)
#define PEPLATEAUMDEL TIME_MS(350)
#define SV2OTIME TIME_MS(15)
#define PRINTTIME TIME_MS(20)
///////////////////
///////////////////

// pAvgShort assumed to have 16ms tau.
#define PAVGSHORTTAU TIME_MS(20)

ctrlStatusT ctrlStatus;
uint16_t lastCycleVol;

int16_t pInst, pAvgShort, pAvgUShort;
// Variables for breath detect.
int16_t bdP1, bdP2;

// Pressure overshoot measurement variables. Both for inspiration and expiration, overshoot measures 
// the difference between the pressure estimation that is used to close the valve (pValveActuation), and the real 
// pressure reached some time after valve is closed (pPlateau).
int16_t pCtrl, pValveActuation, pPlatMax, pPlatInsp, pPlatExp, pPeepActual, pExpOS, pInspOS; // Variables for overshoot measurement.
// Volume overshoot measurement variables. Measure volume difference between valve close time and after valve actuation time.
// Best way to decide when to determine SV2 close time, even in pressure-mode is to measure the volume that produces the desired IP.
// Estimate lung compliance, multiplied by the desired IP it gives the estimated volume for it.
uint16_t lungC, lungR;
int16_t pInspOS3, pInspOS2; // Pressure overshoot during inhalation for each intermediate valve setting.
int16_t vValveActuation, vPlateau, vInspOS;
// Volume quanta. Volume injected on each fixed-time SV2 opening after initial subState.
int pInspVSet, pInspOSVSet;
int16_t vQuanta;
int16_t pQuantaInsp, pQuantaExp;
int16_t pAdj, vAdj;
uint16_t tInsp;
//uint16_t effectiveFlowRate;
// Inverse of the flow rate, scaled by 2^18, in ms/ml.
uint16_t effectiveFlowRateInv;
time_t rCycleTime, rValveActuationTstamp, rVHighActuationTstamp, rVMedActuationTstamp, rVLowActuationTstamp;
// Response time of the valves. For SV2, measure both close and open actuation time.
time_t rSV2ValveORT, rSV2ValveCRT, rSV3ValveORT;
time_t rValveDelayStart, rTimeTmp;
bool initExpSubState, initInspSubState, sv2DelayCheck, sv3DelayCheck, OSCheck, QuantaCheck;
bool OSCheckInt;
// Measurement and compensation of oscillations in PEEP control.
int16_t pPeepErr, pPeepOsc;

void inspOSMeasure(void) {
    uint16_t tmpUVal;
    int16_t tmpVal;
    int8_t setScale;

    switch (pInspOSVSet) {
        case 1:
            setScale = 3*2;
            break;
        case 2:
            setScale = 3*2/2;
            break;
        case 3:
            setScale = 3*2/3;
            break;
        default:
          setScale = 0;    
    }
    
    // Valve setting when measuring OS. Normalize OS for both valves open (3x).
    // Then scale down in use for the actual setting. This produces no difference in constant conditions, but would enhance the behaviour in changing conditions.
    tmpVal = (setScale*(pPlatMax - pValveActuation))>>1;
    if (pInspOS == 0){
        pInspOS = (3*tmpVal)>>2;
    } else {
        pInspOS = (3 * pInspOS + tmpVal) >> 2;
    }
    if (vInspOS < 0) {
        // Volume overshoot should always be > 0.
        vInspOS = 0;
    }
    
    tmpVal = vMeasureGet();
    // Constant is volume at inspiration. Scale for precision.
    if ((pPlatInsp > MPRESSURE_MBAR(4)) && (tmpVal < 2047)) {
        tmpUVal = (pPlatInsp - pPeepActual) >> 1;
        tmpUVal = (((uint24_t) tmpVal) << 6) / tmpUVal;
        // Now IIR.
        if (lungC == 0){
            lungC = (3*tmpUVal)>>2;
        } else {
            lungC = (3 * lungC + tmpUVal) >> 2;
        }
    }
    
    tmpVal = (setScale*(tmpVal - vValveActuation))>>1;
    if (vInspOS == 0){
        vInspOS = (3*tmpVal)>>2;
    } else {
        vInspOS = (3 * vInspOS + tmpVal) >> 2;
    }

    // Calculate also lungR (mbar/l/min).
    // lungR = (pPlatMax - pPlatInsp)/FlowRate at end of inspiration.
    tmpVal = pPlatMax - pPlatInsp;
    tmpVal = ((uint32_t) setScale*tmpVal*effectiveFlowRateInv)>>9;
    if (tmpVal > (200*MPRESSURE_MBAR(1))){
        tmpVal = 200;
    } else if (tmpVal < (2*MPRESSURE_MBAR(1))){
        tmpVal = 2;
    }
    lungR = (3*lungR + tmpVal)>>2;

    DEBUG_PRINT(("\nIPOS LC %d Plat %d FI %d\n", lungC,DBGPCONVERT(pPlatInsp), effectiveFlowRateInv));
}

// Due to difference between open and close response times of the valves, it is
// needed to delay SV2Low open when switching from SV2Med to SV2Low.
void SV2DelayOpen(void){
    if (initInspSubState) {
        OPEN_SV2LOW;
    }
}

// Power-off
void CtrlPowerOff(void) {
    // Clean screen lower line.
    setCursor(0, 1);
    printstrblock("                ");
    DEBUG_PRINT(("POWER-OFF\n"));
    // Now ensure at least once to update monitor with new state.
    BUZZER_OFF;
    CLOSE_SV3;
    CLOSE_SV2;
    BLED_OFF;
    // Force screen refresh.
    lcdPrintTR = true;
    screenMng();
    while (PrintStrBusy());
    screenMng();
    timeDelayMs(50);
    // Wait until I2C idle, then send message.
    MonitorMsgSendBlock(MONSTATE_SLEEP);
    timeDelayMs(50);
    setBacklight(false);
    // Now wait until power button pressed again.
    DEBUG_PRINT(("Wait for key press\n"));
    while (keyRead() != KEYPOWER);
    // Go back to stop.
    ctrlStatus = CTRL_STOP;
    timeDelayMs(50);
    MonitorMsgSendBlock(MONSTATE_STOP);
}

void main(void) {
    uint16_t tmpUVal;
    int16_t tmpVal, tmpVal2;
    int16_t pInspOSScale, vInspOSScale;
#ifdef DEBUG
    time_t printTime;
#endif
    bool tstScreen = true;


    // Initialize the device
    SYSTEM_Initialize();
    // Disable ADC irq.
    PIE1bits.ADIE = 0;
    PIE1bits.ADTIE = 0;

    TMR4_SetInterruptHandler(SV2DelayOpen);

    // If using interrupts in PIC18 High/Low Priority Mode you need to enable the Global High and Low Interrupts
    // If using interrupts in PIC Mid-Range Compatibility Mode you need to enable the Global Interrupts
    // Use the following macros to:
    INTERRUPT_GlobalInterruptEnable();
    // Disable the Global Interrupts
    //INTERRUPT_GlobalInterruptDisable();

    // Initialize.
    aCaptureInit();
    timeInit();

    // First wait for startup. 50ms.
    timeDelayMs(50);

    keyReadInit();
    screenInit();
    I2C2_MuxInit();
    MonitorInit();
    vMeasureInit();

    while (1) {
        char keyTmp;
        while (!SelfTest(tstScreen))
            tstScreen = false;

        tstScreen = false;
        setCursor(0, 0);
        printstrblock("PRESS + TO REPEAT ");
        setCursor(0, 1);
        printstrblock("PRESS - TO EXIT ");

        keyTmp = keyRead();
        while ((keyTmp != KEYMINUS)&&(keyTmp != KEYPLUS)) {
            keyTmp = keyRead();
            MonitorMsgSend(MONSTATE_STOP);
        }
        if (keyTmp == KEYMINUS) {
            break;
        }
    }

    // Clean screen lower line.
    setCursor(0, 1);
    printstrblock("                ");

    while (1) {
        setCursor(0, 1);
        printstrblock("                ");
        timeDelayMs(10);
        setBacklight(true);
        timeDelayMs(10);

        // Now wait until BREATH button pressed.
        lcdPrintTR = true;
        lcdPrintBR = true;
        BLED_ON;
        while (ctrlStatus != CTRL_RUN) {
            // User inputs, screen update.
            MenuMng();
            screenMng();

            if (ctrlStatus == CTRL_SLEEP) {
                CtrlPowerOff();
                setCursor(0, 1);
                printstrblock("                ");
                timeDelayMs(10);
                setBacklight(true);
                timeDelayMs(10);
                // Now wait until BREATH button pressed.
                lcdPrintTR = true;
                lcdPrintBR = true;
                BLED_ON;
            }

            MonitorMsgSend(MONSTATE_STOP);

            if (keyReadEC() == ESCAPE_CODE) {
                if (keyPeek() == KEYBREATH) {
                    // Key Breath pressed.
                    BLED_OFF;
                    ctrlStatus = CTRL_RUN;

                    // Wait until key depressed.
                    while (keyPeek() != -1)
                        ;
                    keyReadInit();
                    break;
                }
            }
        }

        // Wait until monitor free to receive new message.
        while (MonitorMsgBusy());

        // Init all control variables.
        rSV2ValveORT = 20;
        rSV2ValveCRT = 50;
        rSV3ValveORT = 40;
        sv2DelayCheck = false;
        OSCheck = false;
        QuantaCheck = false;
        pExpOS = 10;
        pInspOS = 50;
        pInspOS3 = 50;
        pInspOS2 = 50;
        vInspOS = 50;
        vQuanta = 30;
        pQuantaInsp = 20;
        pQuantaExp = 20;
        lungC = 0;
        lungR = 0;
        pPeepActual = 0;
	pPeepErr = 0;
	pPeepOsc = 0;
	
        sBreath = false;
        // Flow rate in ml/sec.
        //        effectiveFlowRate=freeFlowRateF;
        // Inverse effective flow rate. Scaled by 2^18
        if (freeFlowRateF > 50) {
            effectiveFlowRateInv = ((uint24_t) 1 << 18) / freeFlowRateF;
        }
        IDuration = ((uint16_t) 60 * 1000) / (3 * BPM);
        EDuration = ((uint16_t) 60 * 1000 / BPM) - IDuration;
        lastCycleVol = 0;
        bRateInit();

        // Start periodic message sent.
        if (VentMode == VMODE_PRESSURE) {
            MonitorMsgSendBlock(MONSTATE_RUNP);
        } else {
            MonitorMsgSendBlock(MONSTATE_RUNV);
        }

        // Start.
        rCycleTime = timeGet();
        while (ctrlStatus != CTRL_SLEEP) {
            /////////////////////////////////////////////
            // Inspiration part of the cycle.
            /////////////////////////////////////////////

            intVentMode = VentMode;
            intMaxP = MPRESSURE_MBAR(MaxP);
            intPEEP = MPRESSURE_MBAR(PEEP) + PEEP_COMP + pPeepOsc;
            intBdTrig = MPRESSURE_MBAR(BdTrig);
            intIDuration = TIME_MS(IDuration);
            if (sBreath) {
                intEDuration = TIME_MS(EDuration + 1000);
            } else {
                intEDuration = TIME_MS(EDuration);
            }
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

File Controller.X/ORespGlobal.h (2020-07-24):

/* Author: David Ortiz
 *
 * Created on April 4, 2020, 12:56 PM
 */

#ifndef ORESPGLOBAL_H
#define	ORESPGLOBAL_H

#ifdef	__cplusplus
extern "C" {
#endif

#include "mcc_generated_files/mcc.h"
#include "aCapture.h"
#include "time.h"

// User parameter limits.
#define BPM_MIN 10
#define BPM_MAX 30
#define IP_MIN 4
#define IP_MAX 60
#define PEEP_MIN 4
#define PEEP_MAX 25
    // Breath detect trigger, in mbar.
#define BDT_MIN 1
#define BDT_MAX 8
// Volume limit. With limitations of this equipment volume below 100ml can not be provided with accuracy. Probably lower limit should be higher.
#define VOL_MIN 100
#define VOL_MAX 1500
#define VOL_AMIN 50
// At this moment this is only due to restriction on display.
#define VOL_AMAX 1500

// Default value for volume alarms. +-25%
#define VOL_ALRM_DFL 25
    
// Max Volume overshoot. In mililiters.
#define VOVERSHOOT_LIMIT 25
// Limit for pressure quanta estimation. Needed to saturate quanta measurement to avoid a deathlock.
#define PQUANTA_LIMIT    MPRESSURE_MBAR(8)
// Limit for pressure quanta estimation. Needed to saturate quanta measurement to avoid a deathlock.
#define VQUANTA_LIMIT    90
// Zero volume threshold for aux sensor.
#define ZVOLTH 20

#define PEEP_COMP   MPRESSURE_MBAR(1.0)

    
// Objective time for inspiration.
#define INSP_TIME 500
    //////////////////////////////////////
    // Actuation pins.
    //////////////////////////////////////
#if 0
#define SV2ISOPEN LATAbits.LATA2
#define OPEN_SV2 LATAbits.LATA2 = 1
#define CLOSE_SV2 LATAbits.LATA2 = 0
#else
#define SV2ISOPEN (LATAbits.LATA2|LATCbits.LATC3)
#define OPEN_SV2 LATAbits.LATA2 = 1;LATCbits.LATC3 = 1
#define CLOSE_SV2 LATAbits.LATA2 = 0;LATCbits.LATC3 = 0

#define OPEN_SV2LOW LATAbits.LATA2 = 0;LATCbits.LATC3 = 1
#define OPEN_SV2MED LATAbits.LATA2 = 1;LATCbits.LATC3 = 0
#define SV2LOWISOPEN LATCbits.LATC3
#define SV2MEDISOPEN LATAbits.LATA2

//#define SV2ISOPEN (sv2_pwmval!=0)
//#define OPEN_SV2 sv2_pwmval=100;PWM5_LoadDutyValue(sv2_pwmval)
//#define CLOSE_SV2 sv2_pwmval=0;PWM5_LoadDutyValue(sv2_pwmval)
#endif
    
#define SV3ISOPEN LATAbits.LATA3
#define OPEN_SV3 LATAbits.LATA3 = 1
#define CLOSE_SV3 LATAbits.LATA3 = 0

#define BLED_ON  LATDbits.LATD6 = 1
#define BLED_OFF LATDbits.LATD6 = 0

#define BUZZERISON  LATDbits.LATD0
#define BUZZER_ON  LATDbits.LATD0 = 1
#define BUZZER_OFF LATDbits.LATD0 = 0

#define DEBUG
//#define OCTAVE

#ifdef DEBUG
#define ERROR_CONDITION(k) CLOSE_SV2;CLOSE_SV3;printf("Fatal %d",k)
#else
#define ERROR_CONDITION(k) CLOSE_SV2;CLOSE_SV3;BUZZER_ON; while(1)
#endif
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

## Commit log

2020-04-03 Monitor Pin configuration. NO functionality
2020-04-03 Added pressure functions and first printf
2020-04-03 Added Documentation
    Added Sample program
    [BOM_emergency_ventilator_20200326_v2.xlsx]
2020-04-05 DOR: Added 1/2 IIR filtering on ADC captures.
2020-04-05 Fixed pressure meassure
2020-04-07 Fixes in alarm Start of pressure monitor
2020-04-07 DOR: Added new pressure sensor. 5010.
2020-04-07 DOR: Added proper filtering and handling of ADC. Now three filtered versions of main pressure with 32ms, 64ms and 1s are generated. Simple first order IIR LPF. Moreover ADC has proper sampling settin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
2020-04-08 several updates
    [4mm hose connector.SLDPRT, 6mm hose connector.SLDPRT, block.SLDDRW, block.SLDPRT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]
2020-04-08 DOR: WIP. Adjusted ADC for exact 1KHz sampling frequency with 3 sources, with room for a fourth (it would be interesting to monitor power supply to generate alarm).
2020-04-08 Added sampling filter. Slow and Fast
2020-04-09 DOR: WIP. Implemented valve actuation delay, and prediction on the pressure for compensating for the actuation delay.
2020-04-09 DOR: Refactoring, variable name changes. Added secondary control on IP for better precision. Also added hysteresis on the fixed-time opening of SV2 during the plateau to reduce overshoots, since even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
2020-04-10 DOR: integrated volume measurement. Pre-calibration with a 5l bottle.
2020-04-10 DOR: change PI plateau measurement to take max value during first 60ms after valve close to avoid overshoot if circuit has losses.
2020-04-12 LCD Working. New DOC
    [4mm hose connector.SLDPRT, 6mm hose connector.SLDPRT, Controller.sch, Main_Board_v1.kicad_pcb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]
2020-04-14 Added pressure alarms implementation
2020-04-18 New Schemartics. Clean up monitor
    [Controller.sch, Main_Board_v1.kicad_pcb, Monitor.sch]
2020-04-18 First layout of Monitor
    [Main_Board_v1.kicad_pcb, Monitor.sch]
2020-04-19 Updated Monitor Schematic
    [Monitor.sch]
2020-04-20 Update in the PCB design. New docs and images
    [Controller.sch, Main_Board_v1.kicad_pcb, Monitor.sch, pcb.dwg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]
2020-04-21 First placement of board
    [Controller.sch, Main_Board_v1.kicad_pcb, Monitor.sch, c-1-2834011-2-2-3d.stp]
2020-04-22 Update in PCB: Schematic and Layout
    [Controller.sch, Main_Board_v1.kicad_pcb, Main_Board_v1_BOM_v0_6.csv, Monitor.sch]
2020-04-24 New PCB version; I2C Slave works
    [Controller.sch, Main_Board_v0.kicad_pcb, Main_Board_v0.sch, Main_Board_v1.csv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]
2020-04-25 DOR: WIP added power-off, reorganized information display. Added independent overshoot control during inspiration.
2020-04-25 New V1 placement done. Speed up Monitor to 64 MHz
    [Controller.sch, Main_Board_v1.kicad_pcb, Monitor.sch]
2020-04-26 DOR: WIP added saturation to pressure quanta to avoid deathlock if pquanta goes too high (which would avoid subsequent actuations, and value would not be updated).
2020-04-26 Version 1 of THT PCB
    [Controller.sch, Main_Board_v1-B_Cu.gbr, Main_Board_v1-B_Mask.gbr, Main_Board_v1-B_Paste.gbr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]
2020-04-27 Updated PCB
    [BOM_emergency_ventilator_20200426_v3.xlsx, Controller.sch, Main_Board_v1-B_Cu.gbr, Main_Board_v1-B_Mask.gbr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]
2020-04-28 Updated PCB with extra Valve
    [Controller.sch, Main_Board_v1.kicad_pcb, Main_Board_v1_1-B_Cu.gbr, Main_Board_v1_1-B_Mask.gbr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]
2020-04-29 DOR: added pmax setting also in pressure mode. Optimized ip phase control to avoid oscillations.
2020-05-01 DOR: Added volume-controller pressure mode for more stability.
2020-05-03 First stable version
    [Panel&Board.FCStd, panel_empty.stl]
2020-05-05 DOR: improved control of two SV2 valves.
2020-05-06 preTest with Artificial doctor
    [Controller.sch, Main_Board_v1_1_smd.kicad_pcb, Main_Board_v1_1_smd.sch, Monitor.sch]
2020-05-07 DOR: added mechanical parts. Dampener not used currently
    [Adapter22m_dual.stl, BatterySupport.stl, Dampener_dual.stl, FlowSensor.stl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]
2020-05-07 DOR: added valve and pressure regulator holders. Used in the prototype
    [PresRegHolder.stl, ValvHolderVert.stl, ValvHolderVertSingle.stl]
2020-05-09 DOR: fixed several bugs. Switched back to use averaged pressure to partially compensate problems caused by the pressure wave during valve opening.
2020-05-10 First tests with artificial lung. 70 cases. New PCB THT fixing mounting issues
    [Controller.sch, Controller_old.sch, Main_Board_v1_1_smd.kicad_pcb, Main_Board_v1_2-B_Cu.gbr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]
2020-05-11 Update THT board reducing to class 3
    [Main_Board_v1_1_smd.kicad_pcb, Main_Board_v1_2-B_Cu.gbr, Main_Board_v1_2-B_Mask.gbr, Main_Board_v1_2-B_Paste.gbr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]
2020-05-11 Fixed SilkScreen V1.2 THT
    [Controller.sch, Main_Board_v1_2-B_Cu.gbr, Main_Board_v1_2-B_Mask.gbr, Main_Board_v1_2-B_Paste.gbr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]
2020-05-11 New SMD PCB
    [Controller.sch, Main_Board_v1_1_smd-B_Cu.gbr, Main_Board_v1_1_smd-B_Mask.gbr, Main_Board_v1_1_smd-B_Paste.gbr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]
2020-05-11 DOR: changed max volume to 1500ml.
2020-05-12 DOR: added measurement of sv2 valve close to avoid full flow when switching from med to low flow. Optimized control operation to avoid wrong overshoot check at end of inspiration.
2020-05-13 DOR: improved switch between different SV2 flows with highly resistive lung.
2020-05-16 Released version of SMD PCB
    [BOM_emergency_ventilator_20200426_v4.xlsx]
2020-05-16 Fixed bug in Alarm Very High Pressure. Clean up static definition of variables
    [Main_Board_v1_1_smd.kicad_pcb]
2020-05-17 Fixed power off
2020-05-22 Change PIN IO Allocation for SMD 1_1 board. New Assembly information version
2020-05-26 DOR: added new version with 6mm hole and taper ends
    [flowsensor_6mm.stl]
2020-05-28 DOR: added extra engineering menu, to show valve stats, lung stats, and allow Breath detect trigger to be programmed.
2020-05-28 DOR: fixed error in flow rate calculation
2020-05-30 DOR: added 1 extra second to expiration cycle during spontaneous detected breaths. Changed hold IP to compensate for leaks also in Volume control mode by detecting pressure loss with respect to the p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
2020-05-30 DOR: unified pressure leak compensation during inspiration.
2020-05-31 DOR: added extra comparison to the theoretical plateau pressure, to make leak compensation more conservative.
2020-06-01 New SMD PCB version
    [Controller.sch, Controller_old.sch, Main_Board_v1_2_smd-B_Cu.gbr, Main_Board_v1_2_smd-B_Mask.gbr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]
2020-06-01 Version for SMD 1.2: Added 5V monitor. MIC in CMP1
2020-06-01 Review QFN footprint
    [Main_Board_v1_2_smd-B_Cu.gbr, Main_Board_v1_2_smd-B_Mask.gbr, Main_Board_v1_2_smd-B_Paste.gbr, Main_Board_v1_2_smd-B_SilkS.gbr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]
2020-06-11 Added GPLv2 license
    [Main_Board_v1_2_smd.kicad_pcb, caratula.FCStd]
2020-06-17 DOR: changed program default value, added buzzer test at init, added smart default values for IP/MAXV when changing from pressure to volume control and the other way around.
2020-07-08 New version of PCB with two footprints for MPXV5004 and s other small changes
    [Controller.sch, Controller_old.sch, Main_Board_v1_3_smd-B_Cu.gbr, Main_Board_v1_3_smd-B_Mask.gbr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]
2020-07-08 Updated Assembly instructions

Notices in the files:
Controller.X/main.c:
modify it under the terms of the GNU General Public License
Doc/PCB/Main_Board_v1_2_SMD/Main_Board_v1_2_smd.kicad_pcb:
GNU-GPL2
